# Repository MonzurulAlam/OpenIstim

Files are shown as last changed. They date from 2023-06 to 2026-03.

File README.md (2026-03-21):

# <P align="center"> OpenXstim - Open Source Transcutaneous Current Stimulator 
 
### DEVELOPED BY:
Dr Monzurul Alam <br/>
Profile: https://scholar.google.com.au/citations?user=a2yhqEQAAAAJ&hl=en&oi=ao <br/>
Contact: md.malam@connect.polyu.hk <br/>

### OBJECTIVES:
<P align="justify"> The objective of this project is to develop a miniature transcutaneous electrical stimulator for non-invasive muscle and nerve stimulation.

### DESCRIPTION:
<P align="justify"> Transcutaneous electrical spinal cord stimulation, a non-invasive spinal cord neuromodulation method holds tremendous promise and hope to restore functions in people with paralysis resultant of spinal cord injury (SCI), cerebral palsy (CP), stroke and other neurological conditions. Yet, there are not many options of such stimulation devices compared to conventional electrical stimulators such as neuromuscular electrical stimulator (NMES), transcutaneous electrical nerve stimulator (TENS) and functional electrical stimulator (FES), especially for most people with neurological conditions in the developing world.
<P align="justify">  OpenXstim is an open-source programmable electrical stimulator (constant current) is a non-invasive muscle, nerve or spinal cord stimulation device. OpenXstim can generate up to 128 mA current pulses with a compliance voltage up to 96 V per stimulation channel. The stimulator is capable of generating high-frequency (10 kHz) burst stimulation, required for transcutaneous spinal cord stimulation (tSCS).
<P align="justify"> The stimulator contains 5 primary sections: 1) a power management unit build with a few DC-DC converters to serve necessary power for the stimulator, 2) a Microcontroller unit for easy programming that provides necessary parameters for the stimulation, 3) a control and display unit to vary the stimulation parameters and display the values, 4) a Digital-to-Analog Converter (DAC) to generate voltage stimulation pulses, 5) a Voltage-to-Current converter unit to convert voltage pulses into appropriate current pulse.

Block-Diagram

### DISCLAIMER:
<P align="justify"> The design is offered as it is. Although it has been regorously tested with utmost care and to the best of my knowledge, I do not provide any warranty in any aspect.

### WARNING:
- The design is intended stricktly for research and education purposes.
- The stimulator is not approved for human or animal and cannot be used without receving prior approval from appropriate ethics committee such as Institutional Review Board.
- The stimulator can generate high voltage and under no circumstances it should be placed across the chest or close to the heart.
- The stimulator should never be powered from external adapter, USB or power source while being used or connected to the body.

### LICENSE:
##### Documentation licensed under the Creative Commons Attribution Share Alike (CC BY-SA) 4.0 International License

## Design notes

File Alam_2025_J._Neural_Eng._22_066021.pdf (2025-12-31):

## Journal of Neural Engineering

PAPER • OPEN ACCESS

## OpenXstim: an open-source programmable electrical stimulator for transcutaneous spinal cord stimulation therapy

To cite this article: Monzurul Alam et al 2025 J. Neural Eng. 22 066021

View the article online (https://doi.org/10.1088/1741-2552/ae20c2) for updates and enhancements.

## You may also like

Using a high-frequency carrier does not improve comfort of transcutaneous spinal cord stimulation
Ashley N Dalrymple, Charli Ann Hooper, Minna G Kuriakose et al.

Recording evoked potentials during deep brain stimulation: development and validation of instrumentation to suppress the stimulus artefact
A R Kent and W M Grill

Randomized cortical stimulation could ameliorate locomotive inability in Parkinsonian rats: a pilot study
Rong-Chao Peng, Xiu-Xiu Liu, Ya Ke et al.

This content was downloaded from IP address 175.32.55.112 on 27/11/2025 at 11:42

J. Neural Eng. 22 (2025) 066021 | https://doi.org/10.1088/1741-2552/ae20c2

# Journal of Neural Engineering

OPEN ACCESS

RECEIVED
22 September 2025

REVISED
2 November 2025

ACCEPTED FOR PUBLICATION
18 November 2025

PUBLISHED
27 November 2025

Original content from
this work may be used
under the terms of the
Creative Commons
Attribution 4.0 licence. (https://creativecommons.org/licenses/by/4.0/)

Any further distribution
of this work must
maintain attribution to
the author(s) and the title of the work, journal
citation and DOI.

PAPER

# OpenXstim: an open-source programmable electrical stimulator for transcutaneous spinal cord stimulation therapy

Monzurul Alam¹,2,∗, (https://orcid.org/0000-0003-0987-1999) Vaheh Nazari³
, Md Akhlasur Rahman⁴

, Vijayapriya Arumugam⁵
,
Naveena Narayanan⁵

, Farjana Taoheed⁴

, Md Shofiqul Islam¹, (https://orcid.org/0000-0001-8085-7976) Padmanabhan Thirunavukkarasu⁶ ,
Mohammad Sohrab Hossain⁴ (https://orcid.org/0000-0002-8452-1641) and Alistair McEwan²,7 (https://orcid.org/0000-0001-7597-6372)

1 Bangladesh Health Professions Institute, Savar, Bangladesh
2
School of Biomedical Engineering, University of Sydney, Sydney, New South Wales, Australia
3
School of Human Movement and Nutrition Sciences, University of Queensland, Brisbane, Queensland, Australia 4 Centre for the Rehabilitation of the Paralysed, Savar, Bangladesh
5 Braintree Speciality Clinic, Chennai, India
6 Madras Medical College, Government Institute of Rehabilitation Medicine, Chennai, India
7
Current address: Cerebral Palsy Alliance, The University of Sydney, NSW 2006, Australia
∗
Author to whom any correspondence should be addressed.

E-mail: md.malam@connect.polyu.hk

Keywords: non-invasive electrical stimulation, transcutaneous spinal cord stimulation (tSCS), neuromodulation, neurological injury, rehabilitation

Supplementary material for this article is available online (http://doi.org/10.1088/1741-2552/ae20c2)

Abstract
Objective. Transcutaneous spinal cord stimulation, a non-invasive spinal cord neuromodulation method holds tremendous promise and hope to restore functions in individuals with paralysis resulting from spinal cord injury (SCI), cerebral palsy, stroke and other neurological conditions. Yet, there are relatively few options for such stimulation devices compared to conventional stimulators commonly used for neuromuscular electrical stimulation, transcutaneous electrical nerve stimulation, and functional electrical stimulation, particularly for people with neurological conditions in the developing countries. Approach. In this report, we present OpenXstim, an open-source, twochannel programmable electrical stimulator developed to advance research in non-invasive muscle, nerve, or spinal cord stimulation treatments. Main results. OpenXstim can deliver current pulses up to 110 mA with a compliance voltage of 96 V per channel. In benchtop testing, we found that the stimulator successfully generates high frequency (9 kHz) burst stimulation, a mode commonly used for spinal cord neuromodulation. The stimulator was further tested in two individuals with SCI and showed preliminary indications of functional improvement. However, large controlled trials are needed to establish efficacy. Although special care was taken in the design of the stimulator to ensure user safety, users are strongly warned to handle the device with utmost caution, as it can generate high voltage and current that may cause adverse health effects if not used properly. Significance. This programmable, open-source stimulator offers tangible hope for improving the accessibility of non-invasive neuromodulation treatments for people with paralysis worldwide. The design and complete source-code of the stimulator are freely available online in a public repository: https://github.com/OpenMedTech-Lab/OpenXstim

### 1. Background

Transcutaneous spinal cord stimulation (tSCS) is an emerging non-invasive technique that has shown promising results in enhancing functional recovery across several neurological conditions, including spinal cord injury (SCI) (Tefertiller et al 2022,

Moritz et al 2024, Lucas et al 2025), cerebral palsy (CP) (Hastings et al 2022, Sachdeva et al 2024), stroke (Moshonkina et al 2022, Kreydin et al 2024), and traumatic brain injury (TBI) (Qian et al 2020, Calderone et al 2024). By delivering electrical stimulation through the skin to the spinal cord, tSCS aims to modulate spinal neural circuits and enhance

© 2025 The Author(s). Published by IOP Publishing Ltd

J. Neural Eng. 22 (2025) 066021 | M Alam et al

sensorimotor function. Evidence suggests that tSCS
can lead to significant improvements in movement, muscle strength, and overall functional outcomes, particularly when combined with conventional activity-based rehabilitation methods (Gopaul et al 2025, Suggitt et al 2025). For successful neuromodulation, a single rectangular pulse or burst of tSCS at motor-threshold elicits evoked potentials to the muscles through efferent synaptic pathways (Alam et al 2020, Gelenitis et al 2025). Previous studies have demonstrated that moderate-intensity tSCS applied over the T11-T12 vertebrae can depolarize posterior root and simultaneously elicit bilateral monosynaptic reflexes in the quadriceps, hamstrings, tibialis anterior, and triceps surae muscles (Sayenko et al 2015, Calvert et al 2019, Gordineer et al 2024). It was further demonstrated that monosynaptic posterior root reflexes in extensor and flexor muscles of thigh and leg can be elicited by stimulating L2-S1 spinal segments in upright standing position, and can be modulated during the execution of postural maneuvers (Hofstoetter et al 2018, Bryson et al 2023). Tonic tSCS utilizes charge-balanced, symmetric, biphasic rectangular pulses at sub-threshold strengths to modulate the spinal cord circuits. The frequency of this tonic stimulation generally ranges from 5 to 100 Hz. Recent design includes modulated tSCS with a 5–10 kHz carrier frequency, which can successfully activate spinal circuits in human (Gerasimenko et al 2015, Shamantseva et al 2024), although some studies have found no significant benefit of using high carrier frequencies over conventional waveforms (Manson et al 2020, Dalrymple et al 2023). Recent studies have found that, in case of a disruption of the connection between the brain and the spinal cord, resulting from an injury or disease, motor tasks can be enabled by tSCS to the cervical and/or lumbosacral segments of the spinal cord (Martin 2021, Rahman et al 2022, Alam et al 2023). Modification of spasticity by tonic tSCS was also demonstrated in individuals with SCI (Hofstoetter et al 2020, Alashram et al 2021, Minassian et al 2024). In a recent study, it has also been demonstrated that tSCS can induce rhythmic activities of legs in robotic orthosis driven body-weight support system in upright position in people with complete SCI (Minassian et al 2016, Krenn et al 2023). Furthermore, repetitive gait training along with tSCS promotes long term functional recovery (Esteset al 2021, Comino-Suárez et al 2025). Despite the growing success of tSCS in restoring functions in individuals with various neurological conditions, there are very few stimulators available that can deliver the specific stimulation parameters required—particularly high-frequency stimulation at 5–10 kHz. Furthermore, the ones that are available are expensive, bulky, and require careful laboratory setting and are not suitable for home or outdoor use. To address this a simple, low-cost, open source, programmable electrical stimulator was developed, and step-by-step prototyping of the stimulator was presented to allow others to make their own stimulator for tSCS therapy (Alam 2022). In the present report, an upgraded multichannel stimulator is presented which is capable of current pulse stimulation, crucial for more robust neuromodulation therapy. Several open-source electrical stimulators have been reported (Coelho-Magalh˜aes et al 2022, Trout et al 2023). But, to the best of our knowledge, this is the first open-source electrical stimulator capable of high frequency burst stimulation. Special care has been given to minimize the complexity of the design by using commonly available components so that one can build one’s own stimulator from anywhere in the world. In this report, we have also included two case studies in which participants demonstrated improvements in sensorimotor function following stimulation treatment using the OpenXstim stimulator.

### 2. Methods

### 2.1. Stimulator design

For easy prototyping, the electrical stimulator was designed using commonly available commercial offthe-shelf components. Functional block diagram of the stimulator is shown in figure 1. The stimulator contains 5 primary sections: (1) a power management unit build with a few DC–DC converters to serve necessary power for the stimulator, (2) a Microcontroller unit for easy programming that provides necessary parameters for the stimulation,
(3) a control and display unit to vary the stimulation parameters and display the values, (4) a digital-toanalog converter (DAC) to generate voltage stimulation pulses, (5) a voltage-to-current converter unit to convert voltage pulses into appropriate current pulse. Operations of each of these are described in detail in the following sections.

### 2.2. Power management by DC–DC converters

The stimulator requires different voltages and power ratings for different sections. For instance, while the Microcontroller and display unit require only positive rail, the DAC and V/I circuit require both positive and negative rails to operate. Furthermore, due to the high skin impedance (∼500 Ω at 1 kHz), transcutaneous stimulation requires high compliance voltage to be able to deliver necessary current through the skin. But, for safety and ease of use, these stimulators are commonly powered by a single NiCd/NiMH battery. The presented stimulator is powered by a single 9 V battery with relatively high ampere-hour ratings (>650 mAh) to be able to deliver necessary power. Figure 2 shows the power management circuit of the stimulator. The battery voltage is inverted to negative rail using a charge pump DC–DC converter

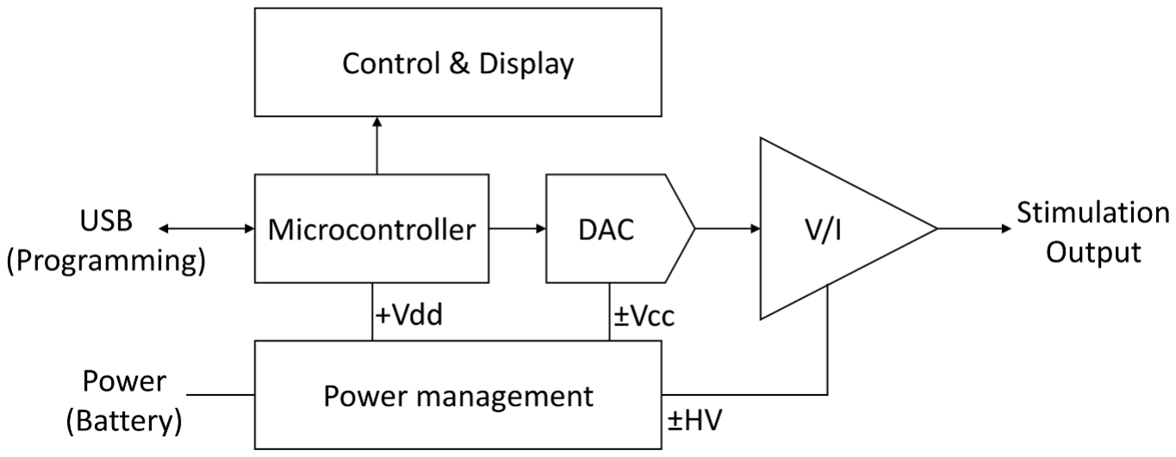
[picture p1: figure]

Figure 1. Block diagram of a transcutaneous electrical stimulator (OpenXstim) for non-invasive electrical stimulation. The stimulator has 5 major sections: a power management unit to serve necessary power for the stimulator, a Microcontroller unit for easy programming stimulation parameters, and a control & display unit to set and display the stimulation parameters, a digital-toanalog converter (DAC) to generate stimulation pulses, a voltage-to-current (V/I) converter unit to convert voltage pulses into appropriate current pulses.

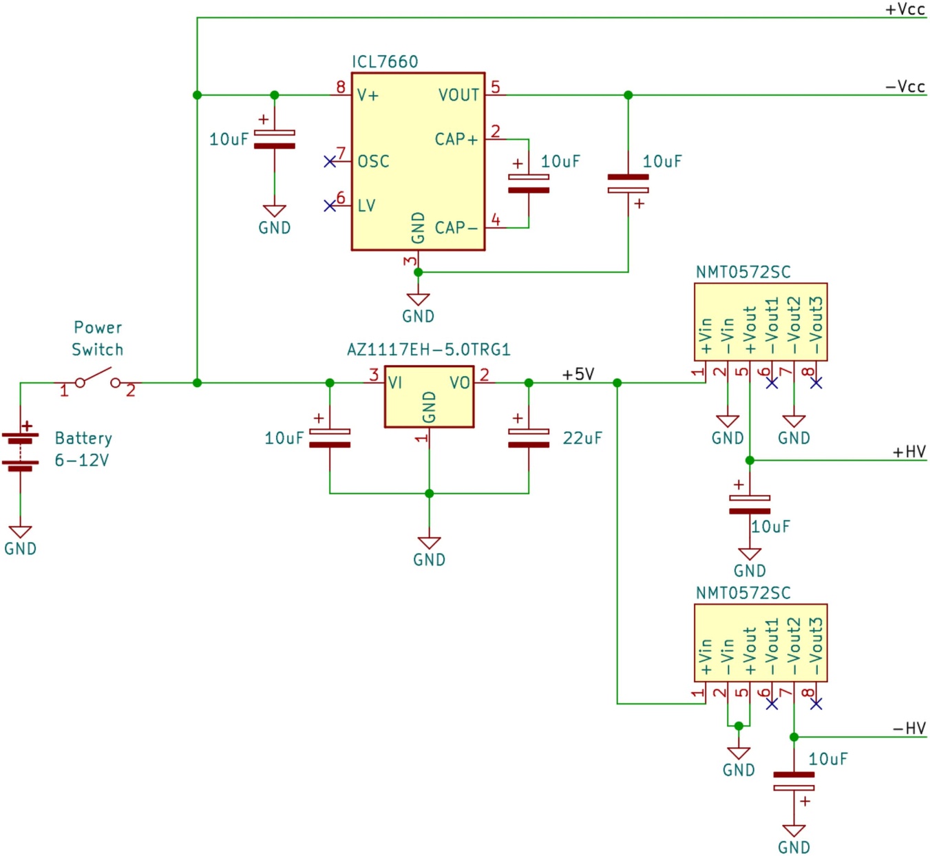
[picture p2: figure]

Figure 2. Schematic diagram of the power management circuit of OpenXstim stimulator. While the circuit allows any voltage between 6 to 12 volts to have stable operation, we recommend using a 9 V 650 mAh battery to power the stimulator.

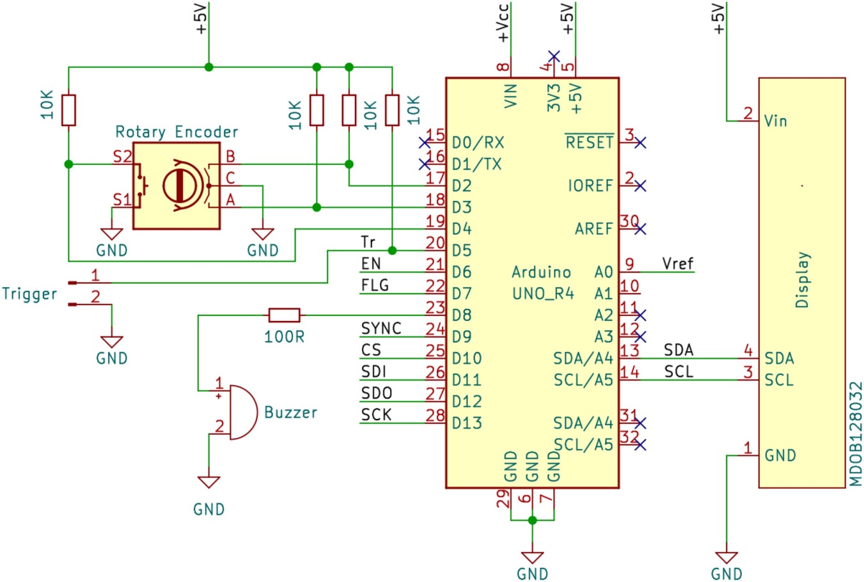
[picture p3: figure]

Figure 3. A rotary encoder and a display unit are wired to Arduino Uno Microcontroller board for quick change and display the stimulation parameters. A digital buzzer is also connected to the Microcontroller to allow audio notifications for different events as per programmed.

(ICL7660S) for the DAC circuit to be able to generate biphasic stimulation pulses. In parallel, to generate high voltage rails, two isolated DC–DC boost converters (NMT0572SC) are used. The boost converters are connected in such a manner to produce both high positive (+HV) and high negative (−HV) voltages. We used the -vout2 of NMT0572SC to get 48 volts rail for V/I converter circuit. A high-voltage 10 µF capacitor was used on each rail to store charge for high-current operation during the active cycle of the stimulation. Since the DC–DC boost converters can only operate with 5-volt input, we used another DC– DC voltage regulator (AZ117EH-5.0TRG1) to power both NMT0572SC. Necessary capacitors with appropriate voltage and charge ratings were used to regulate the voltage for each DC–DC converter chip. For details, please refer to appropriate datasheet provided by the chip manufacturer.

### 2.3. Set and display stimulation parameters

(Microcontroller, Control and display unit)
The core of the stimulator is a very popular open-source Microcontroller board: Arduino Uno. While necessary firmware can be uploaded to the Microcontroller from a computer using a standard USB cable to run the stimulation program, a digital rotary encoder (PEC12R-4025F-S0024) was used to allow quick parameter changes. A rotary encoder typically uses a rotating disk with patterns and a magnetic sensor to produce pulses as the disk turns. Taking advantage of two interrupt pins of Arduino Uno (figure 3 shows the wiring diagram), the output signals of PEC12R-4025F-S0024 rotary encoder sends the microcontroller to specific interrupt service routine (ISR) to increase or decrease output current. This method ensures precise and efficient handling of the encoder’s output by responding immediate pulse changes. The rotary encoder also includes a built-in press-switch function, which allows switching between current intensity and frequency adjustment modes. Pressing the knob activates a subroutine in the firmware (supplementary 1) that enables frequency control using the same rotary count mechanism. The stimulation parameters and other information are displayed to an OLED display (MDOB128032) connect via the I2C bus of the Microcontroller. We used SSD1306 display driver, developed by Adafruit for the OLED display. Figure 3 shows the complete wiring diagram of the PEC12R-4025F-S0024 rotary encoder and MDOB128032 display to the Microcontroller.

### 2.4. Biphasic pulse generation by DAC

To generate bipolar output voltage, a dual channel 12-bit Digital to Analogue Converter (AD5722) was used. The DAC is controlled through a standard 4-wire serial peripheral interface bus. Figure 4 shows the wiring diagram of AD5722 for Arduino Uno Microcontroller. A voltage divider made by two 1k

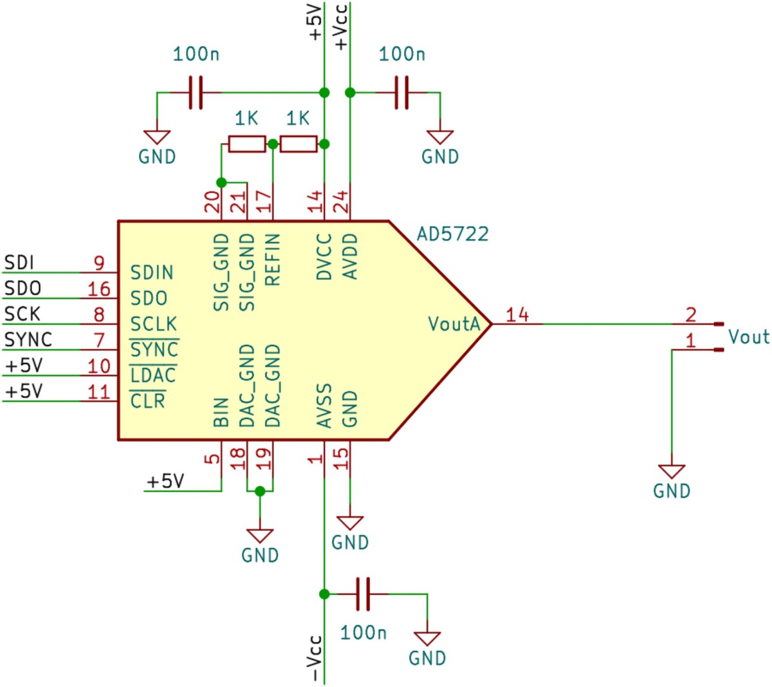
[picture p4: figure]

Figure 4. Schematic diagram of AD8722, a dual channel 12 bit digital-to-analog converter (DAC). For simplicity, only one channel is shown (VoutA).

resistors was used to supply the reference voltage. As mentioned in the power management section, the DAC is supplied with both positive and negative analogue power rails (±5 V) to allow it to generate bipolar voltage stimulation. For bipolar output range, the output voltage expression for AD5722 is shown below:

VOUT = VREF × Gain D
2

N

−

Gain × VREF
2

(1)

where:

D is the decimal equivalent of the value loaded to the DAC
N is the bit resolution (12)
VREF is the reference voltage applied to the REFIN pin (2.5 volt)
Gain is the internal gain (set to 4 for ±5 V output span)

### 2.5. Generating current pulses by

voltage-to-current (V/I) converter
The bipolar voltage output from each DAC channel is converted to constant current using an improved Howland current pump circuit (figure 5). A high-voltage (100 V), high-current (50 mA) operational amplifier (OPA454) was used to deliver the required high rating current pulses for the stimulator. Current pulses were generated by alternating the input voltage (Vin) of the improved Howland current pump circuit. This is done by programming the DAC to output alternating voltages at a stimulation frequency. We also used highly matched 25 kΩ (±0.1%) resistors array (ORNTA2502AT1) to convert the input voltage into a precise output current. In this V/I converter circuit, matched resistors are crucial for maintaining accuracy and stability. The op-amp in the circuit controls the current through the load based on the ratio of the resistors. A 50 Ω current control resistor (Rx) was used to set-up voltage-to-current ratio as shown in the following equation:

IOUT ≈

Vin
Rx

(2)

where:

(R4 + Rx)/R2 = R3/R1;

Ideally, when both positive and negative feedback of the operational amplifier are balanced, an infinite output impedance is achieved. As a result, the output current is simply the ratio of the input voltage to the input impedance which is primarily determined by the current control resistor (Santos et al 2013).

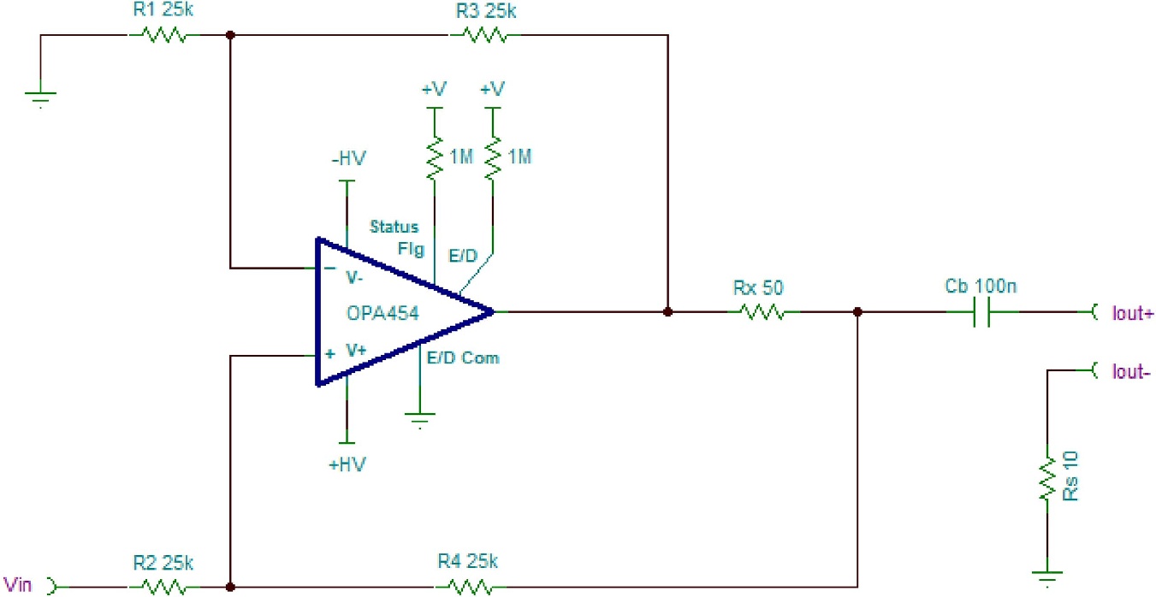
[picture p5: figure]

Figure 5. Improved Howland current pump using high-voltage high-current operational amplifier (OPA454) working as a precise voltage-to-current (V/I) converter circuit. A 25 kΩ quad matched resistor array (ORNTA2502AT1) is necessary to provide stable output current for the stimulator.

Two 1 MΩ pull-up resistors are also required for correct operation of the OPA454 operational amplifier. A 100 nF blocking capacitor is warranted for the protection of DC current to pass through the stimulation electrode in case the stimulator malfunctions. This is an important safety measure one should follow for electrical stimulation of biological tissues (Merrill et al 2005, van Dongen and Serdijn 2016). The stimulation current was also passed through a 10 Ω current sense resistor to allow continuous monitoring of the stimulation pulses.

### 2.6. Prototyping the stimulator

Step 1: Develop and assemble stimulator shield board The complete schematics of the stimulator shield board was developed using an open-source electronic design automation (EDA) software (KiCAD 6.0). Gerber files were generated for prototyping the printed circuit board (PCB) of the stimulator shield board. A two-layer PCB was prototyped through a PCB manufacturer service (JLCPCB, Hong Kong SAR). All the components were sourced and assembled on the PCB through hand soldering. Figure 6(a) shows the 3D model of the assembled stimulator shield board. Standard male header pins were soldered on the bottom of the shield board to allow it to mount on the Microcontroller development board.
Step 2: Stack the stimulator shield on an Arduino Uno board and housing the assembled stimulator
The stimulator shield board was developed with the same footprint of an Arduino Uno development board so that it can easily be stacked on it (figure 6(b)). Arduino Uno is probably the most popular and widely available open-source Microcontroller board, allowing our stimulator to be taken up in most places around the world. Arduino Uno already has onboard female header pins allowing a shield board to be easily mounted on it.
The next step of prototyping is to build a case to house the stimulator to protect the electronics and the users from accidentally touching the components during its operation. We used a computer aided design software (SolidWorks, USA) to design the stimulator’s case, knob, and switch. First, we extracted a 3D model of the stimulator board using EDA software (KiCAD 6.0, USA). The model was then imported into the assembly document, where we began designing the bottom part of the case by creating a new part. The base outline was sketched based on the board’s dimensions; and then extruded to generate a 2 mm thick base. We then added the walls of the case by sketching an outline on the base followed by extrusion to desired height. Functional openings for ventilation and component connections were created. This process was repeated for all components, with each model saved and printed using PLA material on a 3D printer (Adventurer 3, Flashforge, China). Figure 6(c) shows an exploded view of the stimulator.
Step 3: Program the Stimulator
To program the Microcontroller, the Arduino Uno board was connected to a PC via a USB cable. After successfully selecting Arduino Uno board from the menu of Arduino IDE, the firmware was downloaded into the Microcontroller. The program flowchart

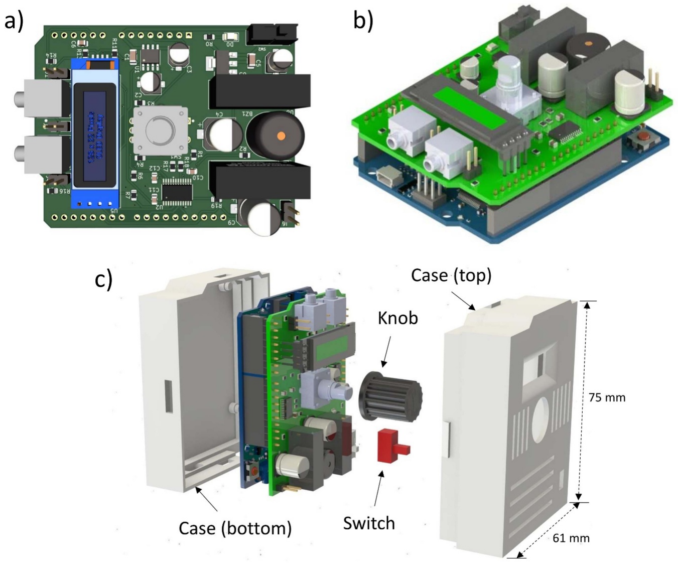
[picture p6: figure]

Figure 6. (a) 3D electronic design automation (EDA) model of assembled stimulator shield board. (b) Stimulator shield board stacked on an Arduino Uno Microcontroller development board through standard header pins. (c) Stimulator case, knob and switch printed using a 3D printer to house the stimulator board.

is shown in figure 7. After the start, stimulation parameters including stimulation frequency, pulse width, burst duration etc. are defined. Next, all the hardware connected to the Microcontroller are initialized by calling appropriate libraries. Then, in a loop N number of biphasic stimulation pulses are generated by writing the defined value to the DAC register. After this loop of stimulation (active burst burst), a delay (inter-burst delay calculated based on the defined stimulation frequency) was added to complete the stimulation cycle. The entire process runs again and again to repeat the stimulation indefinitely until it is powered off.
An ISR was also defined to allow the user quickly to change the stimulation intensity and frequency without re-programming the Microcontroller. Once the rotary encode is rotated, it initiates hardware interrupt of the Microcontroller which triggers the program to break the continuous main loop and jump into the ISR. In the ISR, the program increments or decrements the variable base on the data it reads from the rotary encoder. After that the program returns to the main loop, but now with the updated value of the variable which essentially reflects on the stimulation (an increased or decreased stimulation intensity). The entire source code of the firmware is shared in the stimulator’s GitHub repository as well as attached in supplementary 1.

### 2.7. Benchtop testing the stimulator

The stimulator tested on a benchtop setup. Figure 8 shows the experimental setup. The stimulator was powered by a 9 V battery using barrel adapter. The outputs were connected to two loads, one is 100 Ω resistor and the other is a Randles equivalent circuit of human skin (∼500 Ω impedance at 1 kHz) to test the functionality of the stimulator and emulate the expected operating conditions. A dual channel oscilloscope was used to monitor the voltage across the loads as well as to record the stimulator’s output signal. Stimulation current was varied from 0–140 mA at 20 Hz stimulation (packed with 10 burst pulses at 9 kHz). Data from the oscilloscope were recorded and analyzed to assess the performance of the stimulator in terms of its current, waveform shape, and frequency.

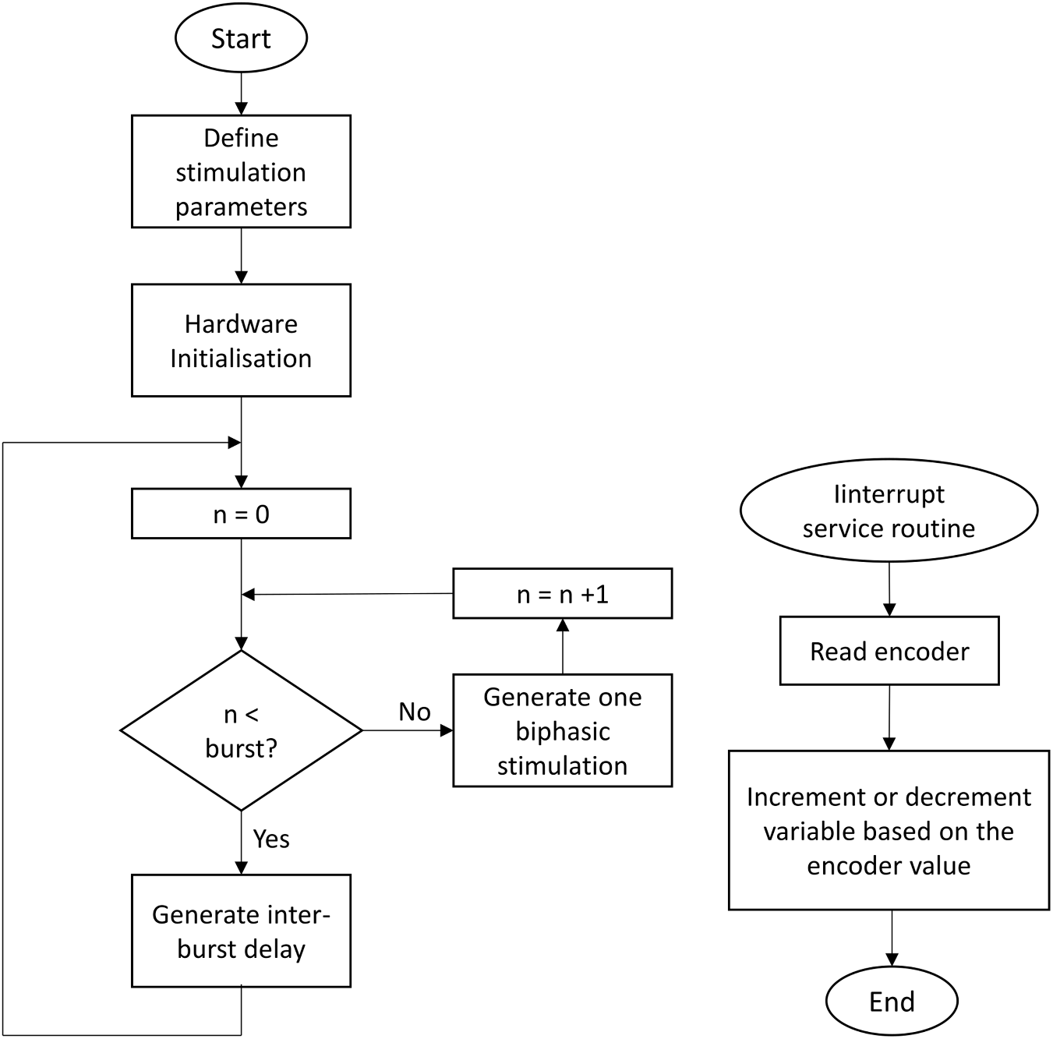
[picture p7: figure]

Figure 7. Flowchart of the high frequency stimulation program.

### 2.8. Clinical case studies

To test the stimulator, we conducted a series of clinical case studies involving individuals with chronic SCI (Trial registration No. ACTRN12625001081404). Eligible participants were required to be at least oneyear post-injury, medically stable, and have previously completed a course of conventional physiotherapy without significant neurological improvement. Individuals with uncontrolled comorbidities, open wounds at stimulation sites, implanted electrical devices, or contraindications to electrical stimulation were excluded. The aim was to evaluate the device’s ability to safely deliver tSCS in combination with conventional physiotherapy, assess participant comfort and tolerance, and observe any preliminary functional changes in a feasibility context. Two self-adhesive stimulation electrodes with a diameter of 3.2 cm (ValuTrode, Axelgaard Manufacturing Co. Ltd) were placed over the interspinous space between T11-T12 and L1-L2, and two internally connected

6.0 × 9.0 cm self-adhesive rectangular return electrodes (Guangzhou Jetta Electronic Medical Device Manufacturing Co. Ltd, China) placed above the iliac crests (Alam et al 2020). Before each stimulation session, the skin was checked to ensure it was free from irritation or wounds. Electrodes were placed with full adhesion and monitored throughout to maintain conductivity and prevent discomfort. These precautions helped minimize the risk of skin irritation or burns during stimulation. Figure 9 shows the electrodes placement and stimulation pattern used for the studies. To ensure safety, standard clinical monitoring was performed throughout each stimulation session to detect any signs of discomfort. During the initial sessions, stimulation was applied at lower intensities and for shorter durations, with gradual increases based on participant tolerance. The electrode sites were inspected regularly before and after each session for any signs of skin irritation or redness.

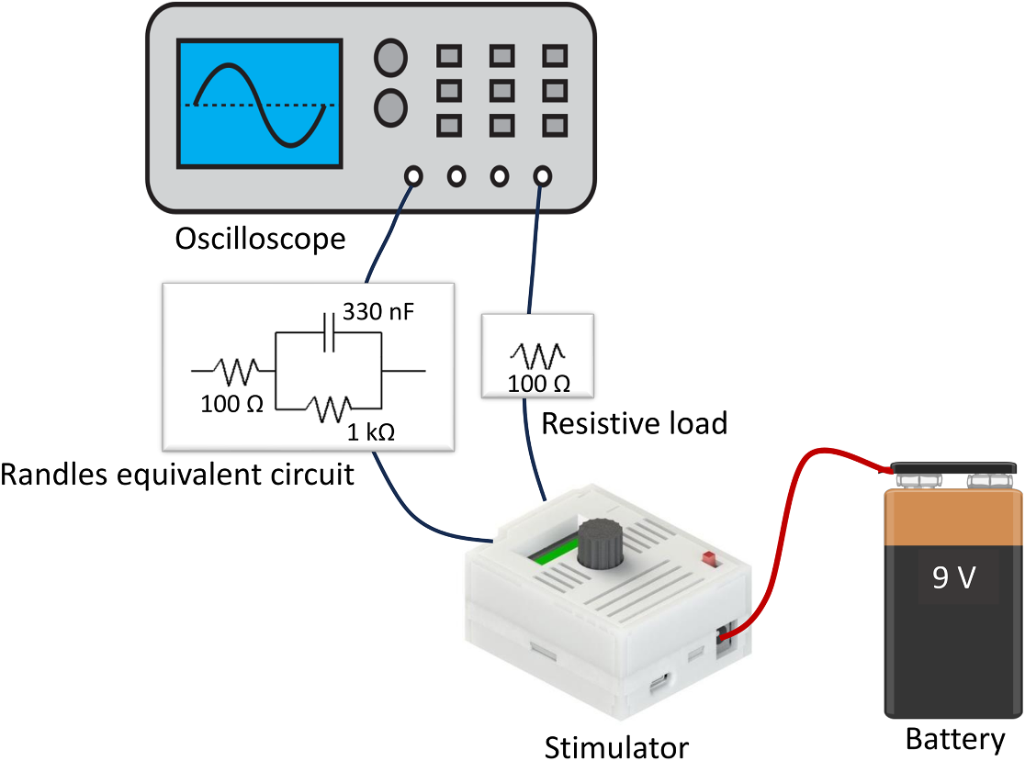
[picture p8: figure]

Figure 8. Benchtop setup for testing the functionality of the OpenXstim stimulator. The stimulator is powered by a 9 V battery. The output channels of the stimulator were connected to an oscilloscope through a resistive load (100 Ω) and Randles equivalent circuit (a 330 nF capacitor and a 1 kΩ resistor in parallel, connected in series with a 100 Ω resistor).

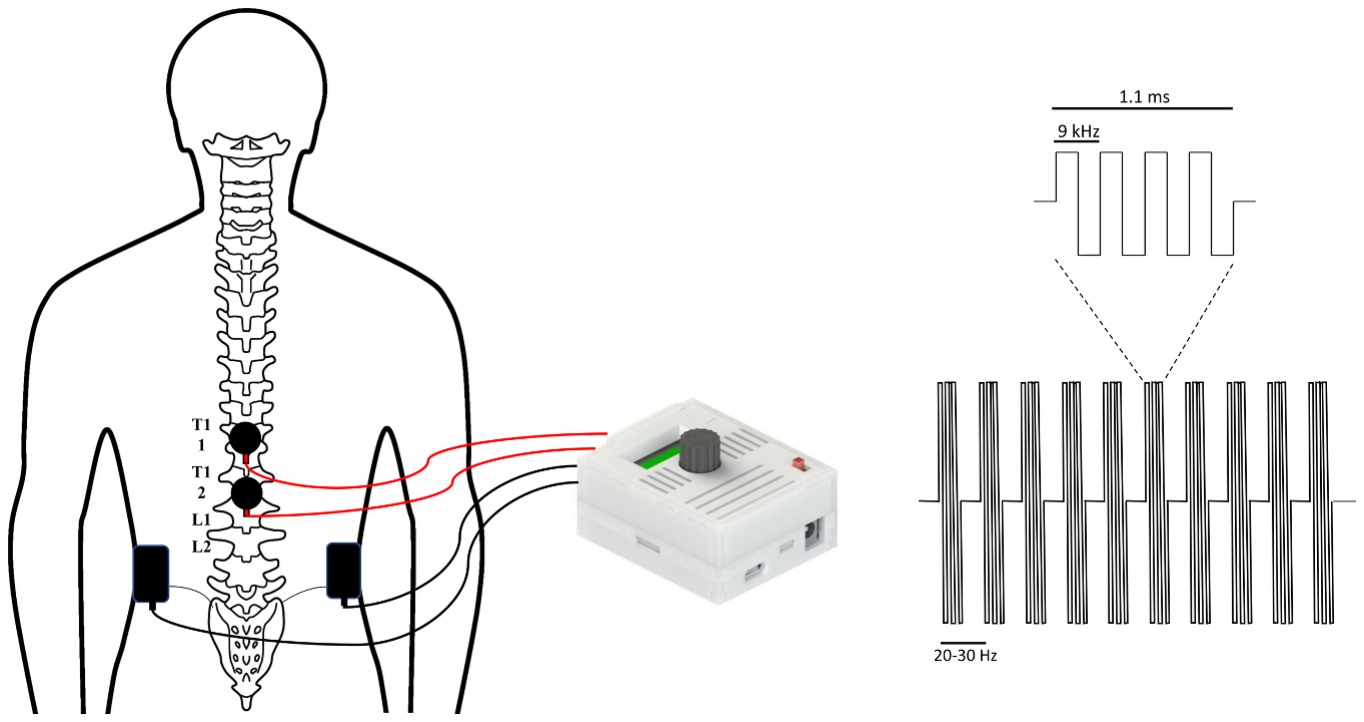
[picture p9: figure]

Figure 9. Electrodes placement of the OpenXstim stimulator (left) and high-frequency burst stimulation pattern (right) used for tSCS therapy.

Case 1:
The study participant was a 16 years old female who sustained a sensorimotor complete (ASIA-A) paraplegia following surgery for an arteriovenous malformation diagnosed at the thoracic 4 (T4) spinal cord. Post-surgery, she received regular physiotherapy upon being released from the hospital after her condition was stabilized. However, her sensorimotor condition did not change, and her paraplegia was considered permanent. Figure 10 shows the study procedure. The study was conducted in accordance with the Declaration of Helsinki and approved (Ref. CRP-BHPI/IRB/04/2025/1054) by the human research ethics subcommittee of the Centre for the Rehabilitation of the Paralyzed, Savar, Bangladesh. At the beginning of the study, a certified physiotherapist assessed the study participant for her sensorimotor scores according to the International

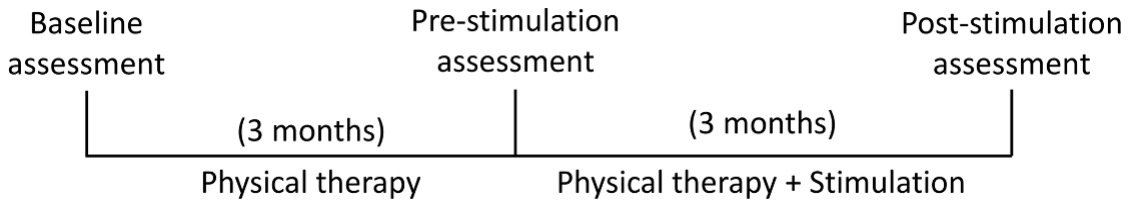
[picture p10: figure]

Figure 10. Study procedure. After baseline assessment of International Standards for Neurological Classification for SCI (ISNCSCI) for residual sensory and motor function, the study participant received conventional physical therapy for a period of 3 months followed by another ISNCSCI assessment. The study participant was then treated with transcutaneous spinal cord stimulation (tSCS) along with the same physical therapy for another 3 months. After the completion of this combinational treatment a final assessment was conducted.

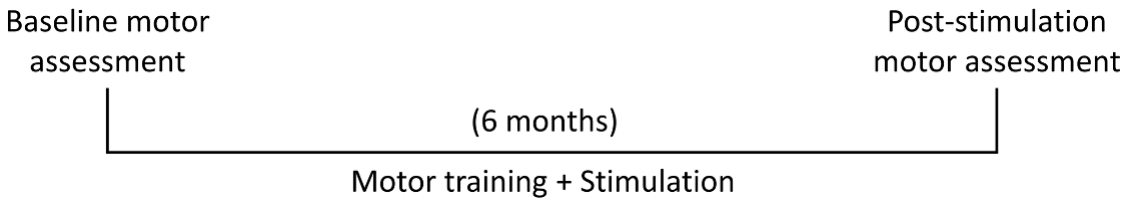
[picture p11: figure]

Figure 11. Study procedure. After baseline motor assessment (MAS), the study participant received a combinational treatment of motor training along with transcutaneous spinal cord stimulation (tSCS) for a period of 6 months. After the completion of this treatment a final motor assessment (MAS) was carried out.

Standards for Neurological Classification for SCI (ISNCSCI). The same physiotherapist also assessed her two more times: at 3 month and 6 month timepoints. During the first phase of treatment, the study participant received a conventional physiotherapy for about 35 min, 3 times a week for 3 months: first 15 min session was sitting balance practice (both static and dynamic condition), then 5 min rest and second 15 min session was standing and sitto-stand practice with the assistance of the physiotherapist. After a thorough sensorimotor assessment (ISNCSCI), in the second phase of the study, the participant received the same physiotherapy but with stimulation tSCS at T11 and L1 spinal levels at 20 Hz, packed with 9 kHz biphasic pulses. The stimulation current was set to a current level that was comfortable to the study participant (40–60 mA) during the physiotherapy session. At the end of the study, the study participant was again assessed (ISNCSCI) for her sensorimotor changes by the same assessor.

Case 2:
A 43 years old female with no significant comorbidities sustained a traumatic SCI following a fall that resulted in a fracture of the T11 spinous process. A posterior spinal fusion from T10 to L1 was performed within 24 h. Post-surgery, she was diagnosed with both motor and sensory complete SCI (ASIA-A) paraplegia, which improved to T11 by discharge. Since her recovery, she had undergone functional electrical stimulation (FES) cycling 1-3 times per week and body-weight supported treadmill walking twice a day. At 2 years post-injury, the ISNCSCI assessment showed limited muscle function: the bilateral hip flexors were graded at 1/5, with very faint movement on the left side. The right knee extensors also showed minimal function, graded at 1/5. All other muscle groups tested were graded at 0/5, indicating no muscle activity in those areas. Figure 11 shows the study procedure. The study was conducted in accordance with the Declaration of Helsinki and was approved (Ref. IEC-MMC/Approval/04032024) by the Institutional Ethics Committee, Madras Medical College, Chennai, India.
At the beginning of the study, a certified physiotherapist assessed the study participant for her sitting function according to the Motor Assessment Scale (MAS). Same physiotherapist also assessed her after 6 month of stimulation assisted motor training. The stimulation intensity and frequency were adjusted according to the task to achieve the desired response. The study participant underwent training 3–5 d a week, focusing on tasks such as sit-to-stand (20 Hz, 30 mA biphasic stimulation), trunk dynamic balance in sitting (20 Hz, 50–70 mA biphasic stimulation), and body-weight supported gait training (30 Hz, 30 mA biphasic stimulation), with each session lasting 20–30 min. The study was approved (Ref. IEC-MMC/Approval/04032024) by the Institutional Ethics Committee, Madras Medical College, Chennai, India.

### 3. Results

### 3.1. OpenXstim: A light-weight versatile stimulator

OpenXstim is an open-source programmable current pulse stimulator capable of transcutaneous stimulation. Figure 12 shows the prototyped stimulator. The stimulator was lightweight (<100 gm), portable

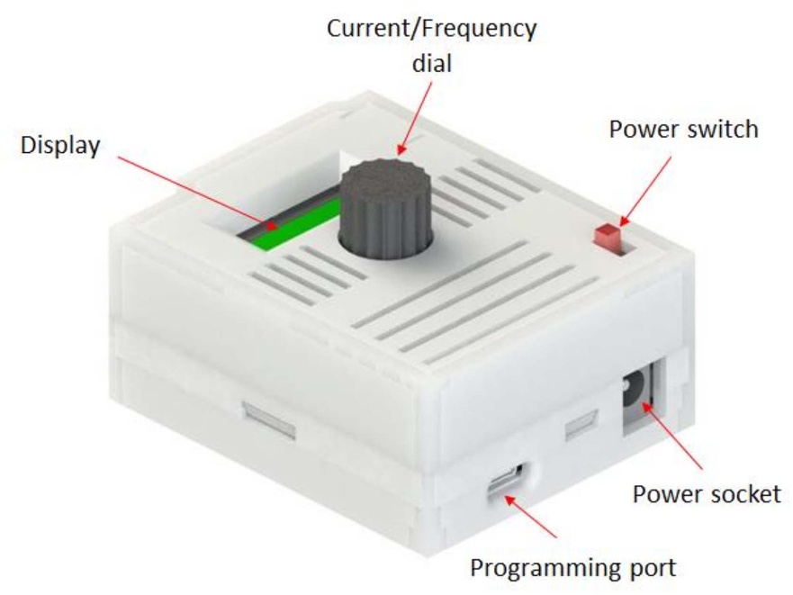
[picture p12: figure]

Figure 12. OpenXstim, open-source transcutaneous electrical stimulator. The stimulator can be powered by a 6–12 V battery with standard barrel jack. Power switch enables the output to deliver stimulation current. The current intensity and frequency are varied using the dial (black) in the center—mode can be selected by pressing the dial knob. The set value is dynamically displayed on the screen of the stimulator.

Table 1. Specifications of the OpenXstim transcutaneous electrical stimulator.

Channel count | 2 channels
Mode of operation | Current pulse
Stimulation waveform Monophasic/Biphasic
| (programmable)
Stimulation intensity | 0–110 mA
Compliance voltage | Maximum 96 V (peak-to-peak)
Pulse duration | Minimum 50 µs (programmable)
Stimulation frequency Maximum 9 kHz (programmable)
Power supply | 6–12 V DC

(battery powered), and easy to use, with participants and clinicians finding it simple to transport and operate. The rotary knob control made to adjust the current and the frequency was straightforward, and the therapists reported no difficulties in using the device. The stimulator was compact enough to be carried and placed in the required treatment locations, and there were no issues with the electrode or cable during the study. The device performed reliably over the six-month usage period, demonstrating strong feasibility and usability. However, an improvement could be made with the battery design—having a built-in, rechargeable battery would eliminate the need for frequent replacements and enhance the overall user experience. Detailed specifications of the stimulator are listed in table 1.

### 3.2. OpenXstim can generate high frequency burst

stimulation
In the present study, both channels of the stimulator were programmed to deliver high frequency burst pulses in-phase for transcutaneous electrical stimulation. The stimulator was tested on a benchtop setup; each channel of the stimulator connected to a load (see Methods section) for its functionality. Figure 13 illustrates the induced voltage across the load for 100 mA stimulation current. Ch 1 is the voltage across the Randles equivalent circuit whereas Ch 2 is the voltage across the resistive load. Both signals show successful biphasic burst stimulation at around 9 kHz.
The biphasic stimulation burst generated by the OpenXstim stimulator contains very short (<1 ns) inter-pulse interval due to the very fast operation of its DAC (see figure 13), a significant improvement from a commercial research stimulator (DS8R, Digitimer, United Kingdom) commonly used for transcutaneous stimulation where minimum inter-pulse interval is 1 µs. Furthermore, unlike many commercial electrical stimulators that uses multiplexed timesharing stimulation of multichannel stimulation (Valtin et al 2016), both stimulation channels of OpenXstim can stimulate simultaneous, providing greater flexibility of stimulation therapy.
The stimulator was also tested for its functionality of delivering required stimulation current at different intensities. Figure 14 shows the set vs measured stimulation currents across two loads. The results show excellent linear fits (R

2 = 0.9987 and 0.9997) of measured current values. However, the current does not appear to reach the set value, indicating a calibration offset. For the stimulation treatment, the current intensity was much lower than the maximum value.

Case 1: Restoration of somatosensory function using OpenXstim stimulator
Our study participant suffered a sensorimotor complete (ASIA-A) paralysis and received conventional
physiotherapy | followed | by | a | combinational

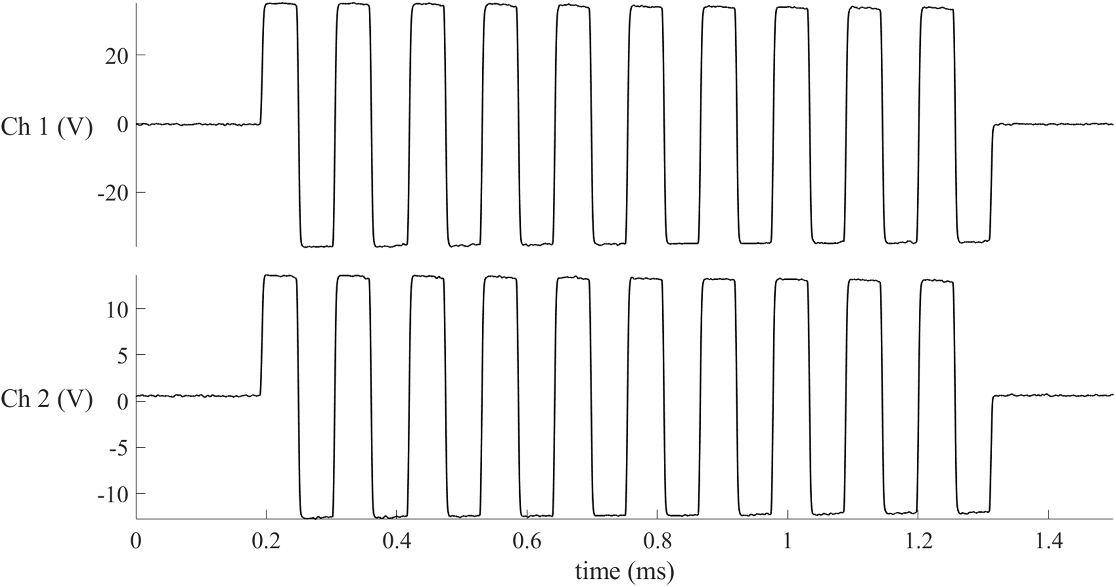
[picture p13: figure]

Figure 13. Induced voltage of 10 biphasic stimulation pulses at around 9 kHz burst stimulation across a Randles equivalent circuit (Ch 1) and a resistive load (Ch 2).

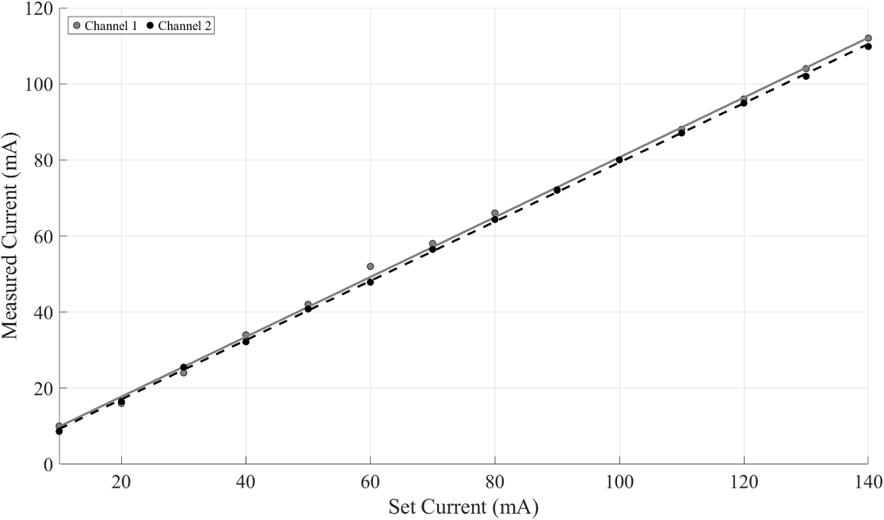
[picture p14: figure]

Figure 14. Set vs measured stimulation currents across loads. Blue line fits the data points measured for Channel 1 and black line fits the data points measured for Channel 2.

physiotherapy and tSCS. After 3 months of conventional physiotherapy (conservative management) without electrical stimulation, the ISNCSCI score remained the same as the baseline (motor and sensory complete ASIA-A). But after 3 months of physiotherapy with tSCS ASIA scale changed to ASIA-B (motor complete but sensory incomplete). Furthermore, the study participant got some sensory improvements as shown in figure 15. By the end of the study her sensory level for neurological injury changed from T4 to T5.
The tSCS therapy delivered by the OpenXstim was found to be well-tolerated, with preliminary indications of sensory improvement below the level of injury. The stimulation current was generally well-tolerated; however, due to the participant’s young age and unfamiliarity with the intervention, initial nervousness was reported in response to the novel sensations induced by tSCS. Over time, with continuous support and reassurance from the caregiver and clinician, the participant gained confidence and became increasingly comfortable as the study progressed.

Case 2: Improvement of motor functions after tSCS therapy
After 6 months of motor training with tSCS therapy delivered by the OpenXstim stimulator, the study participant showed improvements in sitting balance with forward weight shifting, and the study participant is now able to reach forward with better

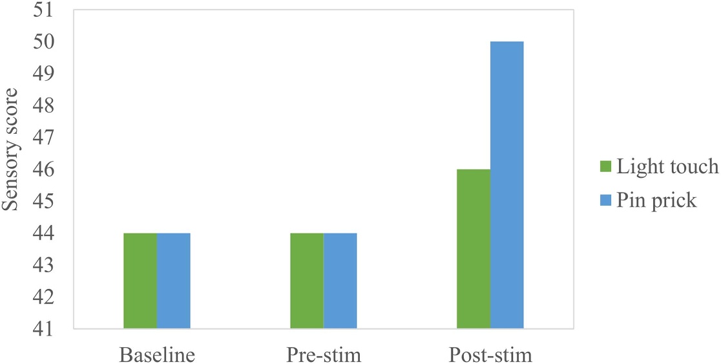
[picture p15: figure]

Figure 15. Total light touch and pin prick sensory scores according to the ISNCSCI at baseline, after 3 months conventional training (pre-stimulation) and 3 months conventional plus stimulation training (post-stimulation).

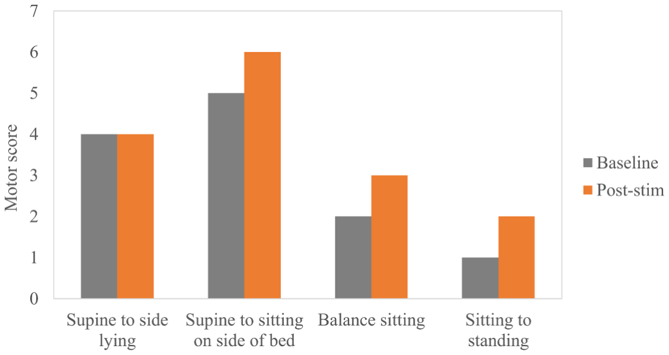
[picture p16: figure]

Figure 16. Baseline vs post-stimulation scores according to the Motor Assessment Scale (MAS) for different posture transitions.

core stability. Figure 16 shows changed in balance sitting and performance in postural transitions (supine to side lying, supine to sitting on the side of the bed and sitting to standing) before and after stimulation assisted motor training according to the MAS. Except supine to side lying, all other functions have improved after the stimulation training.
The tSCS was found to be feasible and safe, with early signs of improved core stability. The stimulation current was generally comfortable; however, when the battery charge depleted, it was not possible to lower the intensity before switching off the stimulator. This direct shutdown caused discomfort for the study participant, highlighting the importance of using high-rate battery that allows slowly reducing intensity prior to turning off the device.

### 4. Discussion

### 4.1. Clinical significance and the need for

accessible neuromodulation devices
Each year, an estimated 250 000–500 000 new cases of SCI are reported globally (Nuechterlein et al 2023), often resulting in life-altering and debilitating conditions. Recent studies have highlighted the potentials of tSCS as an effective neuromodulation therapy not only for SCI rehabilitation (Hofstoetter and Minassian 2022, Rahman et al 2022) but also for a range of neurological conditions, including CP (Gad et al 2021, Hastings et al 2022), TBI (Qian et al 2020, Calderone et al 2024) and Stroke (Moon et al 2024, Zhang et al 2024). Despite its growing therapeutic promise, access to tSCS remains limited due to the high cost, bulkiness, and proprietary nature of most available stimulators. In this report, we present

Table 2. List of electrical stimulators used for non-invasive spinal cord stimulation (tSCS) therapy.

Name | Company | Approval | Channel | Power | Price
Biostim-5 (Grishin et al 2019) | Cosyma Inc. | N/A | 5 | Battery | N/A
NeoStim-5 (Parhizi et al 2021) | | N/A | 5 | Battery | N/A
ARCEX (Samejima et al 2022) | ONWARD
| Medical Inc | FDA | 4 | Battery | N/A
Stimulette r2x (Hofstoetter et al 2021) | Schuhfried
| Medizintechnik
| GmbH | N/A | 2 | Line | N/A
SCONE™ (Kreydin et al 2022) | SpineX Inc. | FDA Breakthrough
| | Device | 2 | Battery | N/A
SCiP (Gad et al 2021) | | | 2 | Battery | N/A
DS8R (Alam et al 2020) | Digitimer Ltd | N/A | 1 | Line | £8,335
OpenXstim | Present report | N/A | 2 | Battery | <$200

OpenXstim, a low-cost, open-source transcutaneous
electrical stimulator designed to improve the accessibility and affordability of spinal cord stimulation— particularly in low- and middle-income countries (LMICs).

### 4.2. Bridging the gap: OpenXstim for global

research equity
The overarching aim of this work is to enhance research capacity, particularly within low-resource settings, by offering an affordable and openly accessible transcutaneous electrical stimulation platform in line with the 2030 UN Sustainable Development Goals. Financial constraints and limited access to proprietary technologies are two major barriers that continue to hinder research and development in these regions, despite the presence of substantial technical expertise and scientific talent (Leal Filho et al 2022). By addressing these barriers, this work seeks to catalyze innovation and enable researchers—especially in LMICs—to design and conduct ethically approved studies using a device tailored to their specific needs. Since the presented stimulator is fully programmable and supports and supports a wide bandwidth of stimulation parameters, it can be easily configured to deliver standard protocols including neuromuscular electrical stimulation, transcutaneous electrical nerve stimulation, and FES, as well as experimental paradigms such as high-frequency tSCS. Table 2 shows the list of transcutaneous electrical stimulators used for non-invasive spinal cord stimulation therapy in people with neurological conditions.

### 4.3. Open-source commitment and design

affordability
The presented stimulator (OpenXstim) provides an easy-accessible tool for non-invasive spinal cord stimulation to arguably for most communities around the world. The design schematics and source code for the stimulator are freely available online, allowing others to replicate or modify the device. All the design files, code and technical details can be freely downloaded from the OpenMedTech-Lab’s

GitHub repository (https://openmedtech-lab.github.io/). (https://openmedtech-lab.github.io/) This open-source approach is a significant step toward making spinal cord stimulation therapy more affordable and accessible, particularly in resourcelimited settings.
Components and modules used to build the OpenXstim stimulator are all listed in table 3. The total component cost of building the stimulator was only US$149.99; however, it can vary based on the market and supplies of the items. Additional costs should be considered for PCB prototyping and 3D printing of stimulator housing, which are significantly lower these days due to worldwide prototyping services. Reference prices and sources of all the components are also listed in table 3. Special care is given to choosing the most commonly available items so that anyone can build the stimulator anywhere in the world. One should, however, check with their local market and supplier for the availability of the components and modules. In case of unavailability, a similar module can be used, but care must be given to connect appropriate circuits and power.

### 4.4. Limitations and ensuring user safety

One of the primary limitations of this work is the small sample size, consisting of only two clinical case studies. The clinical case studies presented in this report are proof-of-concept feasibility tests, not designed to evaluate efficacy. While these cases offer preliminary insights into the feasibility of using OpenXstim for tSCS, they do not allow for generalization of outcomes or statistical significance. A controlled clinical study involving large sample size is necessary to evaluate the effectiveness of the spinal cord neuromodulation intervention delivered by OpenXstim across diverse populations and injury profiles.
An important limitation of this report is the use of different outcome assessment tools across the two case studies. While the ISNCSCI is the goldstandard measure for assessing sensory and motor recovery following SCI, the MAS was used in Case 2 to evaluate functional performance. The MAS

Table 3. Bill of materials (BOM) of OpenXstim with itemized cost in US dollars.

No. | Item name | Description | Unit price | Units | Subtotal
1 | A1 | Arduino UNO | 20.64 | 1 | 20.64
2 | BZ1 | Buzzer | 0.82 | 1 | 0.82
3 | C1–C5 | 10 uF | 0.24 | 5 | 1.2
4 | C8 | 22 uF | 0.75 | 1 | 0.75
5 | C6, C7, C10–C14 | 100 n | 0.24 | 7 | 1.68
6 | D0 | LED | 0.27 | 1 | 0.27
7 | IC1, IC2 | OPA454 | 7.63 | 2 | 15.26
8 | R0 | 270 R | 0.16 | 1 | 0.16
9 | R2 | 100 R | 0.16 | 1 | 0.16
10 | R1, R3, R4, R19 | 10 K | 0.16 | 4 | 0.64
11 | R6, R7, R9–R11, R13 | 1 M | 0.16 | 6 | 0.96
12 | R5, R8 | ORNTA2502AT1 | 7.79 | 2 | 15.58
13 | R12, R15 | 49R9 | 0.16 | 2 | 0.32
14 | R14, R16 | 10 R | 0.16 | 2 | 0.32
15 | R17, R18 | 1 K | 0.16 | 2 | 0.32
16 | SW1 | PEC12R-4025F-S0024 | 2.75 | 1 | 2.75
17 | SW2 | SW_SPDT | 0.72 | 1 | 0.72
18 | U1 | ICL7660S | 2.27 | 1 | 2.27
19 | U2 | AD5722AREZ | 19.39 | 1 | 19.39
20 | U3 | AZ1117EH-5.0TRG1 | 0.75 | 1 | 0.75
21 | U5 | MDOB128032 | 12.61 | 1 | 12.61
22 | U6, U8 | NMT0572SC | 26.21 | 2 | 52.42
| | Total | | | US$149.99

was originally developed and validated for stroke rehabilitation; however, it has also been applied in individuals with SCI to evaluate sitting balance and functional transitions (Jørgensen et al 2011). Given that the participant in Case 2 primarily trained for sit-to-stand, dynamic trunk control, and gait tasks, MAS provided a sensitive measure of functional improvement that may not be captured by ISNCSCI motor scores (Tharu et al 2023). Nevertheless, the inconsistency in assessment tools limits the direct comparability between cases, and future studies should employ standardized and validated outcome measures specific to SCI rehabilitation.
Another key limitation is the absence of long-term safety data for the use of OpenXstim in chronic stimulation. Although short-term usage did not result in adverse effects in the current cases, prolonged or repeated exposure to electrical stimulation requires careful evaluation, especially given the potential for skin irritation, burns, or electrode-related complications. For additional safety, in our design, we used a DC blocking capacitor in each stimulation channel. This ensures stopping any prolonged constant voltage or current to be delivered to through the stimulation electrodes in the event of stimulator malfunction (van Dongen and Serdijn 2016). Additionally, to prevent risks such as uneven current distribution, burns, and electrode movement, it is essential to ensure that electrodes are securely and properly attached to the skin (Nussbaum et al 2017). Regularly inspect the gel for any signs of dryness or loss of adhesion, especially at the edges, and reapply as needed to maintain consistent contact. This helps to ensure proper conductivity and prevent the gel from lifting, which can lead to increased current density and other safety hazards.
In both case studies, managing electrical currents to prevent discomfort highlights the importance of controlling the intensity of stimulation. An additional feature that could be implemented to address this issue is the integration of current ramp-up/rampdown functionality, a standard feature in many electrical stimulation systems (Nussbaum et al 2017). This feature gradually increases or decreases the electrical current, allowing for a smoother transition in muscle activation and preventing abrupt changes that could cause discomfort or injury. Ramping up the current gradually ensures that the muscles and tissues can adapt to the stimulation, particularly in sensitive individuals or during long-term usage. Similarly, ramping down the current allows for a safe reduction in intensity, which can help prevent sudden muscle release, thus improving safety and comfort throughout the therapy.
The stimulator’s operability was also assessed during 30 min of continuous use, corresponding to the typical therapeutic session duration. Moderate heating was observed in the 5.0 V linear regulator (AZ117EH-5.0TRG1) and minimal heating in the DC–DC boost converter (NMT0572SC), indicating acceptable thermal performance. Future versions may eliminate the linear regulator by using a regulated 5 V power source to improve efficiency and reduce heat buildup.

### 4.5. Future enhancements and expanded

applications
The current OpenXstim firmware does not include real-time impedance monitoring, which is a standard feature in many clinical-grade stimulation devices. Continuous impedance monitoring is crucial for ensuring consistent and safe electrical delivery, especially in dynamic environments where electrode-skin contact may fluctuate due to movement, sweating, or drying of conductive gel (Vargas Luna et al 2015). Although our design utilizes a constant current source that dynamically adjusts its output current based on the variable load, the absence of real-time impedance monitoring may increase the risk of uneven current distribution, discomfort, or localized skin heating. Integrating impedance monitoring would not only enhance safety but also improve the precision of stimulation delivery and help prevent unintended fluctuations in current during therapy sessions. Our hardware design already includes circuitry— such as current sensing resistor and analog-to-digital converter—that enables load impedance measurement (see supplementary 1). However, this functionality has not yet been implemented in the firmware. Incorporating impedance monitoring into the firmware should be prioritized in future iterations of the device.
The calibration offset of the stimulation current is primarily due to small mismatches in the resistor network of the improved Howland current pump circuit. Despite using high-precision matched resistors, these mismatches—along with the influence of the current control resistor and the finite open-loop gain of the operational amplifier—can reduce output impedance and introduce load-dependent variations, especially at higher stimulation intensities (Ghorbani and Nahvi 2019). Future improvements may include tighter tolerance components and firmware-based closed-loop calibration to enhance accuracy and linearity.
Although the stimulator includes a power switch that can disconnect it is power anytime, adding an additional emergency stop switch would be beneficiary for the user. Additional features, such as wireless control and signal monitoring, can be easily incorporated to enhance the functionality and usability of the stimulator. Since the stimulator is an Arduino Uno shield, using an Uno board with wireless capabilities such as Minima or WiFi would allow it to function as a wireless stimulator. This modification would enable its use in extended applications, such as brain-computer interface control or electronic bypass of SCI, as we demonstrated previously (Alam et al 2014, Li et al 2014, McGeady et al 2022).

### 5. Conclusion

OpenXstim was designed using commercially available components to ensure global accessibility and ease of replication. Bench testing confirmed the device’s ability to deliver reliable high frequency burst stimulation, while preliminary clinical case studies demonstrated its potential to improve sensory and motor function in individuals with chronic paralysis. OpenXstim addresses a critical gap in the availability of accessible neuromodulation technologies— particularly for use in low-resource settings. Its open-source design, including hardware schematics, firmware, and documentation, is freely available (https://github.com/OpenMedTech-Lab/OpenXstim) to support reproducibility and customization. OpenXstim represents a promising step toward democratizing spinal cord stimulation therapy and expanding global research capacity in neuromuscular rehabilitation.

Data availability statement

Design source files and additional documentation related to the OpenXstim stimulator are available in the online public repository: https://github.com/OpenMedTech-Lab/OpenXstim (https://github.com/OpenMedTech-Lab/OpenXstim)
Technical data set of OpenXstim v1.0 available at https://doi.org/10.1088/1741-2552/ae20c2/data1.

Acknowledgment

We sincerely thank the study participants for their time, valuable feedback, and contribution to the evaluation of the OpenXstim stimulator.

Conflict of interest

The authors declare no competing interests.

Funding

The authors did not receive any funding for this work.

Authors’ contributions

M.A. wrote the main manuscript text with parts from V.N., M.A.R. and V.A. N.N., F.T. and M.S.I helped with the case studies. P.T. and M.S.H. examined and validated the clinical data. A.M. revised and corrected the main manuscript and provided inputs to improve the manuscript. All authors reviewed the final manuscript.

Consent for publication

Informed consent for publication of anonymized data and results was obtained from all the study participants.

Disclaimers

The stimulator design is provided as-is and, despite careful development and extensive testing, no warranties are offered regarding its performance or safety. The authors cannot be held liable for any accidents or misuse of the stimulator.

Ethics approval and consent to participate

The studies involving human participants were conducted in accordance with the ethical standards and with the 1964 Helsinki Declaration and its later amendments. Ethical approvals were obtained for both case studies.

Users’ safety notes

- The design is intended exclusively for research and educational purposes.
- The stimulator has not been approved for use on humans or animals without prior authorization from a relevant ethics committee, such as an Institutional Review Board.
- The stimulator can produce high voltage. It must never be positioned across the chest, head, or in close proximity to the heart.
- The stimulator should never be powered through an external adapter, USB, or any other power source while in use or when connected to the body.
- Stimulation electrodes should be securely attached to the skin, and the gel remains intact to prevent uneven current distribution, and the risk of skin irritation or burns.

License

All the source files of the stimulator are licensed under the Creative Commons Attribution Share Alike 4.0 International License.

ORCID iDs

Monzurul Alam (https://orcid.org/0000-0003-0987-1999) 0000-0003-0987-1999 (https://orcid.org/0000-0003-0987-1999) Md Shofiqul Islam (https://orcid.org/0000-0001-8085-7976) 0000-0001-8085-7976 (https://orcid.org/0000-0001-8085-7976) Mohammad Sohrab Hossain
0000-0002-8452-1641 (https://orcid.org/0000-0002-8452-1641)
Alistair McEwan (https://orcid.org/0000-0001-7597-6372) 0000-0001-7597-6372 (https://orcid.org/0000-0001-7597-6372)

References

Alam M 2022 An easy-to-build transcutaneous electrical stimulator for spinal cord stimulation therapy
Alam M, Chen X, Zhang Z, Li Y and He J 2014 A brain-machine-muscle interface for restoring hindlimb locomotion after complete spinal transection in rats PLoS One 9 (https://doi.org/10.1371/journal.pone.0103764) e103764 (https://doi.org/10.1371/journal.pone.0103764)
Alam M, Ling Y T, Rahman M A, Wong A Y L, Zhong H, Edgerton V R and Zheng Y-P 2023 Restoration of over-ground walking via non-invasive neuromodulation therapy: a single-case study J. Clin. Med. 12 (https://doi.org/10.3390/jcm12237362) 7362 (https://doi.org/10.3390/jcm12237362)

Alam M, Ling Y T, Wong A Y L, Zhong H, Edgerton V R and Zheng Y-P 2020 Reversing 21 years of chronic paralysis via non-invasive spinal cord neuromodulation: a case study Ann. Clin. Transl. Neurol. 7 (https://doi.org/10.1002/acn3.51051) 829–38 (https://doi.org/10.1002/acn3.51051)
Alashram A R et al 2021 Transcutaneous spinal cord stimulation effects on spasticity in patients with spinal cord
injury: a systematic review J. Spinal Cord Med.
46 (https://doi.org/10.1080/10790268.2021.2000200) 1–8 (https://doi.org/10.1080/10790268.2021.2000200)
Bryson N, Lombardi L, Hawthorn R, Fei J, Keesey R, Peiffer J D and Seánez I 2023 Enhanced selectivity of transcutaneous ˜ spinal cord stimulation by multielectrode configuration J. Neural Eng. 20 (https://doi.org/10.1088/1741-2552/ace552) 046015 (https://doi.org/10.1088/1741-2552/ace552)
Calderone A, Cardile D, Gangemi A, De Luca R, Quartarone A, Corallo F and Calabr`o R S 2024 Traumatic brain injury and neuromodulation techniques in rehabilitation: a scoping review Biomedicines 12 (https://doi.org/10.3390/biomedicines12020438) 438 (https://doi.org/10.3390/biomedicines12020438)
Calvert J S, Manson G A, Grahn P J and Sayenko D G 2019 Preferential activation of spinal sensorimotor networks via lateralized transcutaneous spinal stimulation in neurologically intact humans J. Neurophysiol.
122 (https://doi.org/10.1152/jn.00454.2019) 2111–8 (https://doi.org/10.1152/jn.00454.2019)
Coelho-Magalh˜aes T, Fachin-Martins E, Silva A, Azevedo Coste C and Resende-Martins H 2022 Development of a high-power capacity open source electrical stimulation system to enhance research into FES-assisted devices: validation of FES cycling Sensors 22 (https://doi.org/10.3390/s22020531) 531 (https://doi.org/10.3390/s22020531)
Comino-Suárez N, Moreno J C, Megía-García A, Del-ama A J, ´
Serrano-Munoz D, Avenda ˜ | no-Coy J, Gil-Agudo ˜ | A, ´
Alcobendas-Maestro M, López-López E and Gómez-Soriano J 2025 Transcutaneous spinal cord stimulation combined with robotic-assisted body weight-supported treadmill training enhances motor score and gait recovery in incomplete spinal cord injury: a double-blind randomized controlled clinical trial J. Neuroeng. Rehabil. 22 (https://doi.org/10.1186/s12984-025-01545-8) 15 (https://doi.org/10.1186/s12984-025-01545-8)
Dalrymple A N, Hooper C A, Kuriakose M G, Capogrosso M and Weber D J 2023 Using a high-frequency carrier does not improve comfort of transcutaneous spinal cord stimulation
J. Neural Eng. 20 (https://doi.org/10.1088/1741-2552/acabe8) 016016 (https://doi.org/10.1088/1741-2552/acabe8)
Estes S, Zarkou A, Hope J M, Suri C and Field-Fote E C 2021 Combined transcutaneous spinal stimulation and locomotor training to improve walking function and reduce spasticity in subacute spinal cord injury: a randomized study of clinical feasibility and efficacy J. Clin. Med.
10 (https://doi.org/10.3390/jcm10061167) 1167 (https://doi.org/10.3390/jcm10061167)
Gad P, Hastings S, Zhong H, Seth G, Kandhari S and
Edgerton V R 2021 Transcutaneous spinal neuromodulation reorganizes neural networks in patients with cerebral palsy Neurotherapeutics 18 (https://doi.org/10.1007/s13311-021-01087-6) 1953–62 (https://doi.org/10.1007/s13311-021-01087-6)
Gelenitis K et al 2025 Non-invasive transcutaneous spinal cord stimulation programming recommendations for the treatment of upper extremity impairment in tetraplegia Neuromodulation 28 (https://doi.org/10.1016/j.neurom.2024.05.005) 162–73 (https://doi.org/10.1016/j.neurom.2024.05.005)
Gerasimenko Y, Gorodnichev R, Moshonkina T, Sayenko D, Gad P and Reggie Edgerton V 2015 Transcutaneous electrical spinal-cord stimulation in humans Ann. Phys. Rehabil. Med. 58 (https://doi.org/10.1016/j.rehab.2015.05.003) 225–31 (https://doi.org/10.1016/j.rehab.2015.05.003)
Ghorbani R and Nahvi M 2019 Analysis of performance of Howland AC current source for electrical impedance spectro-tomography Sens. Imaging 20 (https://doi.org/10.1007/s11220-019-0251-1) 28 (https://doi.org/10.1007/s11220-019-0251-1)
Gopaul U, Bayley M T and Kalsi-Ryan S 2025 Combined activity-based therapy and cervical spinal cord stimulation: active ingredients, targets and mechanisms of actions to optimize neurorestoration of upper limb function after cervical spinal cord injury Physiother. Res. Int.
30 (https://doi.org/10.1002/pri.70036) e70036 (https://doi.org/10.1002/pri.70036)
Gordineer E A, Stokic D S and Krenn M J 2024 Distinguishing reflex from non-reflex responses elicited by transcutaneous spinal stimulation targeting the lumbosacral cord in healthy individuals Exp. Brain Res. 242 (https://doi.org/10.1007/s00221-024-06790-2) 959–70 (https://doi.org/10.1007/s00221-024-06790-2)
Grishin A A, Moshonkina T R, Bobrova E V and Gerasimenko Y P 2019 A device for the rehabilitation therapy of patients with motor pathology using mechanotherapy, transcutaneous electrical stimulation of the spinal cord, and biological feedback Biomed. Eng. 53 (https://doi.org/10.1007/s10527-019-09914-z) 227–30 (https://doi.org/10.1007/s10527-019-09914-z)
Hastings S, Zhong H, Feinstein R, Zelczer G, Mitrovich C, Gad P and Edgerton V R 2022 A pilot study combining noninvasive spinal neuromodulation and activity-based neurorehabilitation therapy in children with cerebral palsy Nat. Commun. 13 (https://doi.org/10.1038/s41467-022-33208-w) 5660 (https://doi.org/10.1038/s41467-022-33208-w)
Hofstoetter U S, Freundl B, Binder H and Minassian K 2018 Common neural structures activated by epidural and transcutaneous lumbar spinal cord stimulation: elicitation of posterior root-muscle reflexes PLoS One 13 (https://doi.org/10.1371/journal.pone.0192013) e0192013 (https://doi.org/10.1371/journal.pone.0192013) Hofstoetter U S, Freundl B, Danner S M, Krenn M J, Mayr W, Binder H and Minassian K 2020 Transcutaneous spinal cord stimulation induces temporary attenuation of spasticity in individuals with spinal cord injury J. Neurotrauma
37 (https://doi.org/10.1089/neu.2019.6588) 481–93 (https://doi.org/10.1089/neu.2019.6588)
Hofstoetter U S, Freundl B, Lackner P and Binder H 2021 Transcutaneous spinal cord stimulation enhances walking performance and reduces spasticity in individuals with multiple sclerosis Brain Sci. 11 (https://doi.org/10.3390/brainsci11040472) 472 (https://doi.org/10.3390/brainsci11040472)
Hofstoetter U S and Minassian K 2022 Transcutaneous spinal cord stimulation: advances in an emerging non-invasive strategy for neuromodulation J. Clin. Med. 11 (https://doi.org/10.3390/jcm11133836) 3836 (https://doi.org/10.3390/jcm11133836) Jørgensen V, Elfving B and Opheim A 2011 Assessment of unsupported sitting in patients with spinal cord injury Spinal Cord 49 (https://doi.org/10.1038/sc.2011.9) 838–43 (https://doi.org/10.1038/sc.2011.9)
Krenn M J, White J M, Stokic D S and Tansey K E 2023 Neuromodulation with transcutaneous spinal stimulation reveals different groups of motor profiles during robot-guided stepping in humans with incomplete spinal cord injury Exp. Brain Res. 241 (https://doi.org/10.1007/s00221-022-06521-5) 365–82 (https://doi.org/10.1007/s00221-022-06521-5)
Kreydin E I et al 2024 A pilot study of the effect of transcutaneous spinal cord stimulation on micturition-related brain activity and lower urinary tract symptoms after stroke J. Urol.
211 (https://doi.org/10.1097/JU.0000000000003776) 294–304 (https://doi.org/10.1097/JU.0000000000003776)
Kreydin E, Zhong H, Lavrov I, Edgerton V R and Gad P 2022 The effect of non-invasive spinal cord stimulation on anorectal function in individuals with spinal cord injury: a case series Front. Neurosci. 16 (https://doi.org/10.3389/fnins.2022.816106) 816106 (https://doi.org/10.3389/fnins.2022.816106)
Leal Filho W et al 2022 An assessment of requirements in investments, new technologies, and infrastructures to achieve the SDGs Environ. Sci. Eur. 34 (https://doi.org/10.1186/s12302-022-00629-9) 58 (https://doi.org/10.1186/s12302-022-00629-9)
Li Y, Alam M, Guo S, Ting K H and He J 2014 Electronic bypass of spinal lesions: activation of lower motor neurons directly driven by cortical neural signals J. Neuroeng. Rehabil. 11 (https://doi.org/10.1186/1743-0003-11-107) 107 (https://doi.org/10.1186/1743-0003-11-107) Lucas K et al 2025 Non-invasive spinal neuromodulation enables stepping in children with complete spinal cord injury Brain148 (https://doi.org/10.1093/brain/awaf115) 3290–99 (https://doi.org/10.1093/brain/awaf115)
Manson G A, Calvert J S, Ling J, Tychhon B, Ali A and
Sayenko D G 2020 The relationship between maximum tolerance and motor activation during transcutaneous spinal stimulation is unaffected by the carrier frequency or vibration Physiol. Rep. 8 (https://doi.org/10.14814/phy2.14397) e14397 (https://doi.org/10.14814/phy2.14397)
Martin R 2021 Utility and feasibility of transcutaneous spinal cord stimulation for patients with incomplete SCI in therapeutic settings: a review of topic Front. Rehabil. Sci. 2 (https://doi.org/10.3389/fresc.2021.724003) 724003 (https://doi.org/10.3389/fresc.2021.724003) McGeady C, Vucˇkovi´c A, Singh Tharu N, Zheng Y-P and Alam M 2022 Brain-computer interface priming for cervical transcutaneous spinal cord stimulation therapy: an exploratory case study Front. Rehabil. Sci. 3 (https://doi.org/10.3389/fresc.2022.896766) 896766 (https://doi.org/10.3389/fresc.2022.896766)
Merrill D R, Bikson M and Jefferys J G R 2005 Electrical stimulation of excitable tissue: design of efficacious and safe protocols J. Neurosci. Methods 141 (https://doi.org/10.1016/j.jneumeth.2004.10.020) 171–98 (https://doi.org/10.1016/j.jneumeth.2004.10.020)
Minassian K, Freundl B, Lackner P and Hofstoetter U S 2024 Transcutaneous spinal cord stimulation neuromodulates pre- and postsynaptic inhibition in the control of spinal spasticity Cell Rep. Med. 5 (https://doi.org/10.1016/j.xcrm.2024.101805) 101805 (https://doi.org/10.1016/j.xcrm.2024.101805)
Minassian K, Hofstoetter U S, Danner S M, Mayr W, Bruce J A, McKay W B and Tansey K E 2016 Spinal rhythm generation by step-induced feedback and transcutaneous posterior root stimulation in complete spinal cord-injured individuals Neurorehabil. Neural Repair. 30 (https://doi.org/10.1177/1545968315591706) 233–43 (https://doi.org/10.1177/1545968315591706)
Moon Y et al 2024 Noninvasive spinal stimulation improves walking in chronic stroke survivors: a proof-of-concept case series Biomed. Eng. Online 23 (https://doi.org/10.1186/s12938-024-01231-1) 38 (https://doi.org/10.1186/s12938-024-01231-1)
Moritz C et al 2024 Non-invasive spinal cord electrical stimulation for arm and hand function in chronic tetraplegia: a safety and efficacy trial Nat. Med.
30 (https://doi.org/10.1038/s41591-024-02940-9) 1276–83 (https://doi.org/10.1038/s41591-024-02940-9)
Moshonkina T R, Zharova E, Ananev S, Shandybina N, Vershinina E, Lyakhovetskii V, Grishin A, Shlyakhto E and Gerasimenko Y 2022 A new technology for recovery of locomotion in patients after a stroke Dokl. Biochem. Biophys. 507 (https://doi.org/10.1134/S1607672922340087) 353–6 (https://doi.org/10.1134/S1607672922340087)
Nuechterlein A, Feng L, Yehia A and Illes J 2023 Strengths, gaps, and future directions on the landscape of ethics-related research for spinal cord injury Spinal Cord 61 (https://doi.org/10.1038/s41393-023-00897-z) 477–82 (https://doi.org/10.1038/s41393-023-00897-z) Nussbaum E L, Houghton P, Anthony J, Rennie S, Shay B L and Hoens A M 2017 Neuromuscular electrical stimulation for treatment of muscle impairment: critical review and recommendations for clinical practice Physiother. Can. 69 (https://doi.org/10.3138/ptc.2015-88) 1–76 (https://doi.org/10.3138/ptc.2015-88)
Parhizi B, Barss T S and Mushahwar V K 2021 Simultaneous cervical and lumbar spinal cord stimulation induces facilitation of both spinal and corticospinal circuitry in humans Front. Neurosci. 15 (https://doi.org/10.3389/fnins.2021.615103) 615103 (https://doi.org/10.3389/fnins.2021.615103)
Qian Q et al 2020 Restoration of arm and hand functions via noninvasive cervical cord neuromodulation after traumatic brain injury: a case study Brain Injury 34 (https://doi.org/10.1080/02699052.2020.1850864) 1–10 (https://doi.org/10.1080/02699052.2020.1850864)
Rahman M A, Tharu N S, Gustin S M, Zheng Y-P and Alam M 2022 Trans-spinal electrical stimulation therapy for functional rehabilitation after spinal cord injury: review J. Clin. Med. 11 (https://doi.org/10.3390/jcm11061550) 1550 (https://doi.org/10.3390/jcm11061550)
Sachdeva R, Girshin K, Shirkhani Y and Gad P 2024 Beyond pediatrics: noninvasive spinal neuromodulation improves motor function in an adult with cerebral palsy Bioelectron. Med. 10 (https://doi.org/10.1186/s42234-023-00133-2) 1 (https://doi.org/10.1186/s42234-023-00133-2)
Samejima S, Caskey C D, Inanici F, Shrivastav S R, Brighton L N, Pradarelli J, Martinez V, Steele K M, Saigal R and Moritz C T 2022 Multisite transcutaneous spinal stimulation for walking and autonomic recovery in motor-incomplete tetraplegia: a single-subject design Phys. Ther.
102 (https://doi.org/10.1093/ptj/pzab228) pzab228 (https://doi.org/10.1093/ptj/pzab228)
Santos S, Schlebusch T and Leonhardt S 2013 Simulation of a current source with a Cole-Cole load for multi-frequency electrical impedance tomography Annual Int. Conf. IEEE Engineering in Medicine and Biology Society pp 6445–8 Sayenko D G, Atkinson D A, Dy C J, Gurley K M, Smith V L, Angeli C, Harkema S J, Edgerton V R and Gerasimenko Y P 2015 Spinal segment-specific transcutaneous stimulation differentially shapes activation pattern among motor pools in humans J. Appl. Physiol. 118 (https://doi.org/10.1152/japplphysiol.01128.2014) 1364–74 (https://doi.org/10.1152/japplphysiol.01128.2014)
Shamantseva N, Timofeeva O, Semenova V, Andreeva I and Moshonkina T 2024 Transcutaneous spinal cord stimulation modulates quiet standing in healthy adults: stimulation site and cognitive style matter Front. Neurosci.
18 (https://doi.org/10.3389/fnins.2024.1467182) 1467182 (https://doi.org/10.3389/fnins.2024.1467182)
Suggitt J, Symonds J and D’Amico J M 2025 Safety and effectiveness of multisite transcutaneous spinal cord stimulation combined with activity-based therapy when delivered in a community rehabilitation setting: a real-world pilot studySafety and effectiveness of multisite transcutaneous spinal cord stimulation combined with activity-based therapy when delivered in a community rehabilitation setting: a real-world pilot study Neuromodulation 28 (https://doi.org/10.1016/j.neurom.2025.01.005) 1144–56 (https://doi.org/10.1016/j.neurom.2025.01.005)
Tefertiller C, Rozwod M, VandeGriend E, Bartelt P, Sevigny M and Smith AC 2022 Transcutaneous electrical spinal cord stimulation to promote recovery in chronic spinal cord injury Front. Rehabil. Sci. 2 (https://doi.org/10.3389/fresc.2021.740307) 740307 (https://doi.org/10.3389/fresc.2021.740307)
Tharu N S, Alam M, Ling Y T, Wong A Y and Zheng Y-P 2023 Combined transcutaneous electrical spinal cord stimulation and task-specific rehabilitation improves trunk and sitting functions in people with chronic tetraplegia Biomedicines 11 (https://doi.org/10.3390/biomedicines11010034) 34 (https://doi.org/10.3390/biomedicines11010034)
Trout M A, Harrison A T, Brinton M R and George J A 2023 A portable, programmable, multichannel stimulator with high compliance voltage for noninvasive neural stimulation of motor and sensory nerves in humans Sci. Rep.
13 (https://doi.org/10.1038/s41598-023-30545-8) 3469 (https://doi.org/10.1038/s41598-023-30545-8)
Valtin M, Kociemba K, Behling C, Kuberski B, Becker S and Schauer T 2016 RehaMovePro: a versatile mobile stimulation system for transcutaneous FES applications Eur.
J. Trans. Myol. 26 (https://doi.org/10.4081/ejtm.2016.6076) 6076 (https://doi.org/10.4081/ejtm.2016.6076)
van Dongen M N and Serdijn W A 2016 Does a coupling capacitor enhance the charge balance during neural stimulation? An empirical study Med. Biol. Eng. Comput. 54 (https://doi.org/10.1007/s11517-015-1312-9) 93–101 (https://doi.org/10.1007/s11517-015-1312-9)
Vargas Luna J L, Krenn M, Cortés Ramírez J A and Mayr W 2015 Dynamic impedance model of the skin-electrode interface for transcutaneous electrical stimulation PLoS One
10 (https://doi.org/10.1371/journal.pone.0125609) e0125609 (https://doi.org/10.1371/journal.pone.0125609)
Zhang J, Wang M, Alam M, Zheng Y-P, Ye F and Hu X 2024 Effects of non-invasive cervical spinal cord
neuromodulation by trans-spinal electrical stimulation on cortico-muscular descending patterns in upper extremity of chronic stroke Front. Bioeng. Biotechnol. 12 (https://doi.org/10.3389/fbioe.2024.1372158) 1372158 (https://doi.org/10.3389/fbioe.2024.1372158)

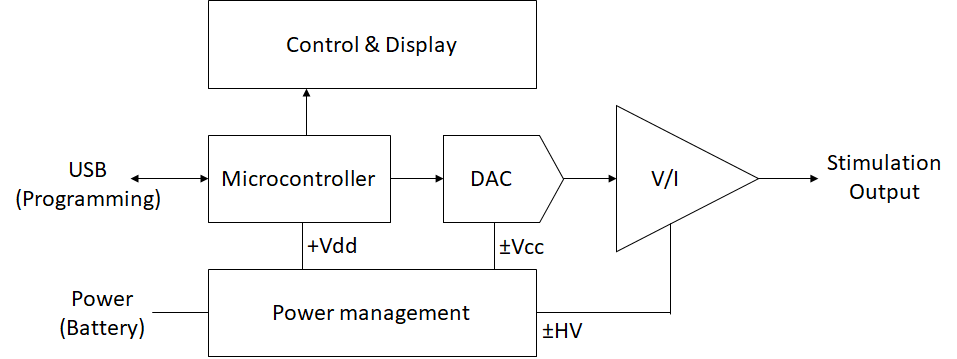
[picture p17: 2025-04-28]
BlockDiagram.png

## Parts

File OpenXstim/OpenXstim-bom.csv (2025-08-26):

Comment | Designator | Footprint
Buzzer | BZ1 | Buzzer_Beeper:Buzzer_12x9.5RM7.6
10uF | C2, C3 | Capacitor_SMD:CP_Elec_5x5.3
10uF | C1, C5 | Capacitor_SMD:C_1206_3216Metric
22uF | C8 | Capacitor_SMD:CP_Elec_5x5.4
10uF | C4, C9 | Capacitor_SMD:CP_Elec_8x10.5
100n | C6, C7, C10, C11, C12, C13, C14 | Capacitor_SMD:C_0805_2012Metric
0.1uF | C15, C16 | Capacitor_SMD:C_0805_2012Metric
LED | D0 | LED_SMD:LED_1206_3216Metric
OPA454 | IC1, IC2 | RehabExo:SO08GP
Test_2 | J1 | Connector_PinHeader_2.54mm:PinHeader_1x02_P2.54mm_Vertical
MJ-2506N | J2, J3 | RehabExo:CUI_MJ-2506N
Test_1 | J4 | Connector_PinHeader_2.54mm:PinHeader_1x02_P2.54mm_Vertical
Ref | J5 | Connector_PinHeader_2.54mm:PinHeader_1x02_P2.54mm_Vertical
Trigger | J6 | Connector_PinHeader_2.54mm:PinHeader_1x02_P2.54mm_Vertical
270R | R0 | Resistor_SMD:R_0805_2012Metric
100R | R2 | Resistor_SMD:R_0805_2012Metric
10K | R1, R3, R4, R19 | Resistor_SMD:R_0805_2012Metric
ORNTA2502AT1 | R5, R8 | RehabExo:ORN_VIS
100K | R6, R7 | Resistor_SMD:R_0805_2012Metric
1M | R9, R10, R11, R13 | Resistor_SMD:R_0805_2012Metric
49R9 | R12, R15 | Resistor_SMD:R_0805_2012Metric
10R | R14, R16 | Resistor_SMD:R_0805_2012Metric
1K | R17, R18 | Resistor_SMD:R_0805_2012Metric
PEC12R-4025F-S0024 | SW1 | RehabExo:ENC_PEC12R-4025F-S0024
SW_SPDT | SW2 | RehabExo:SW_MINI-SPDT-SW
LT1054 | U1 | Package_SO:SOIC-8_3.9x4.9mm_P1.27mm
AD5722AREZ | U2 | RehabExo:RE_24_ADI
AZ1117EH-5.0TRG1 | U3 | Package_TO_SOT_SMD:SOT-223
MDOB128032 | U5 | RehabExo:MDOB128032GV-WI
NMT0572SC | U6, U8 | RehabExo:NMT0572SC

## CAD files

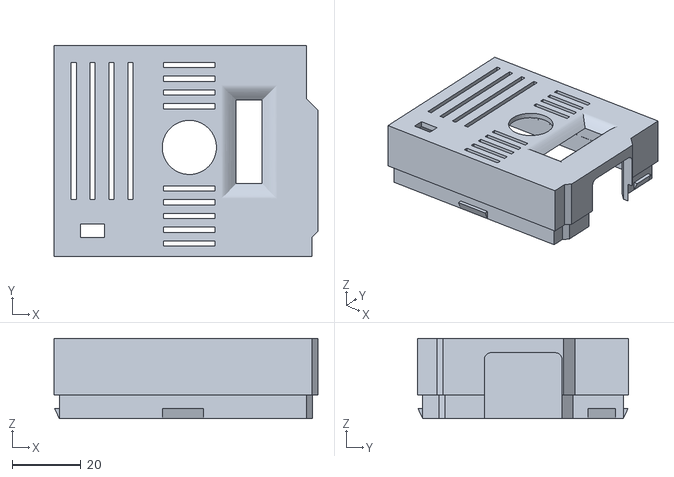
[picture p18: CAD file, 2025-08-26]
OpenXstim/Housing/OpenExostimV2_Top.STL
77.0 x 61.6 x 23.4

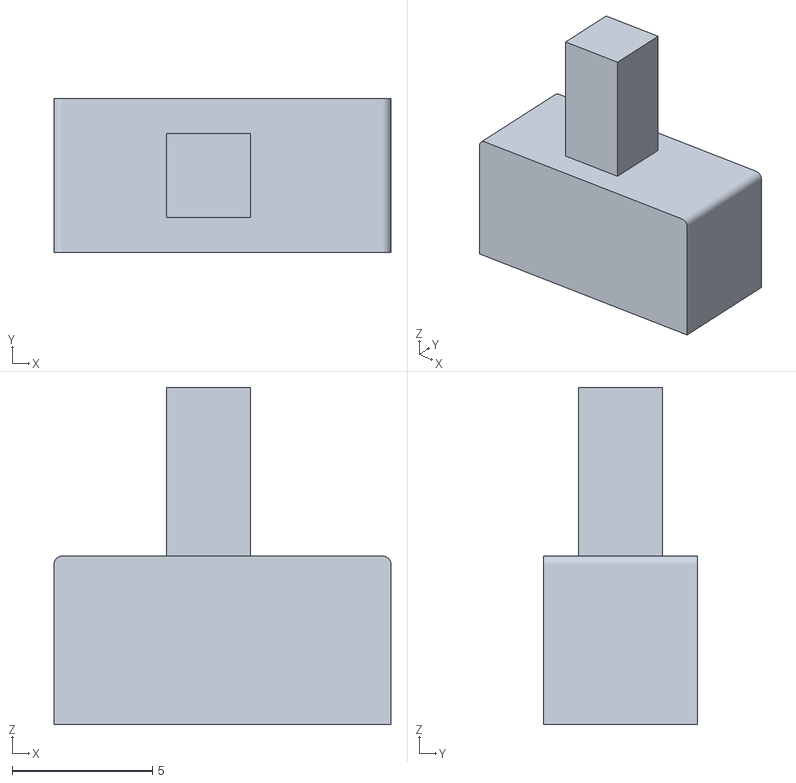
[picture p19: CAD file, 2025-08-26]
OpenXstim/Housing/OpenExoStimV2_Switch.STL
12.0 x 5.50 x 12.0

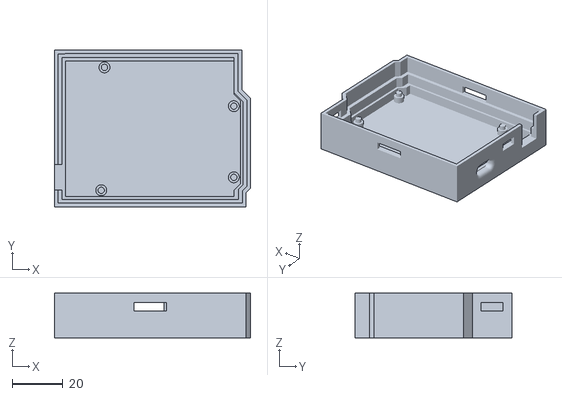
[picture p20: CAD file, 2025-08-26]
OpenXstim/Housing/OpenExoStimV2_Base.STL
77.0 x 61.6 x 17.5

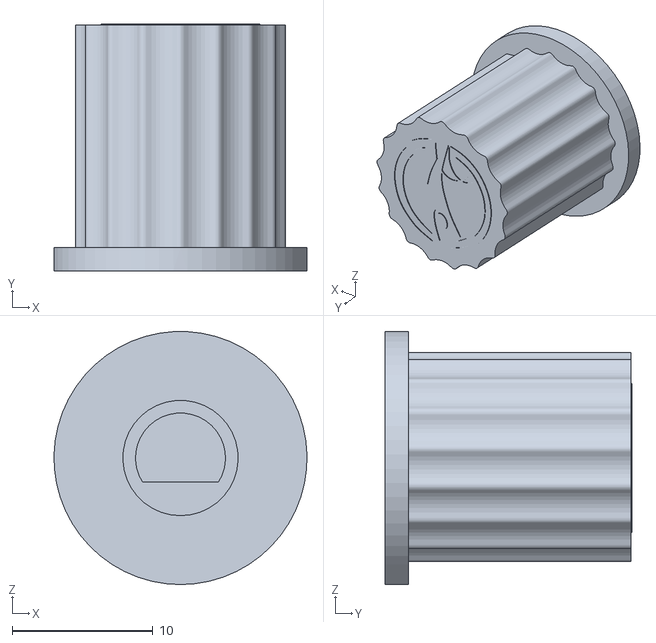
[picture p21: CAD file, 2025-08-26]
OpenXstim/Housing/OpenExoStim_Nob.STL
18.0 x 17.6 x 18.0

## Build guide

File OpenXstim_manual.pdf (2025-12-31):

## OpenXstim v1.0

# __________________________________________________

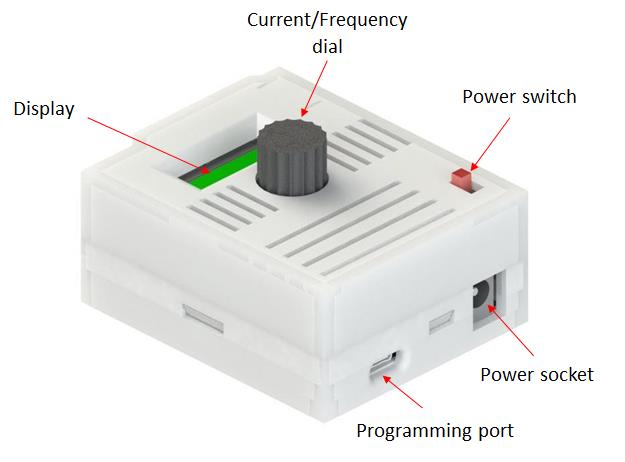
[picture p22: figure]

P a g e 1 | 10

Reference Manual

Description

OpenXstim is a dual-channel programmable constant current stimulator for transcutaneous electrical stimulation. The stimulator is capable of delivering up to 100 mA of biphasic current at a maximum of 10kHz stimulation frequency for each stimulation channel simultaneously. The stimulator board is designed as a popular Arduino Uno shield (recommended to use Arduino uno r4 minima) with pin-to-pin capability for easy programming and operation. An on-board rotary encoder also allows manual control of the stimulation intensity. The stimulation current is automatically sensed by the microcontroller and displayed on an on-board display.

Specifications

- Dimensions: 6.86 cm x 5.33 cm (Arduino Uno Shield)
- Current intensity: 0 – 110 mA (per channel)
- Compliance voltage: ±48 volt
- Stimulation frequency: up-to 10kHz
- Compatibility: Arduino Uno
- Idle bias current: 50 mA
- Full-load supply current: 260 mA
- Supply voltage: 6 – 12 volts DC (preferred: 9V 650 mAh battery)

Warnings

This device is intended for EDUCATION AND RESEARCH PURPOSES ONLY. It is not approved by any regulatory authority for medical or other uses. The user assumes all responsibility for injury or damage due to the misuse of this device.

Design

# __________________________________________________

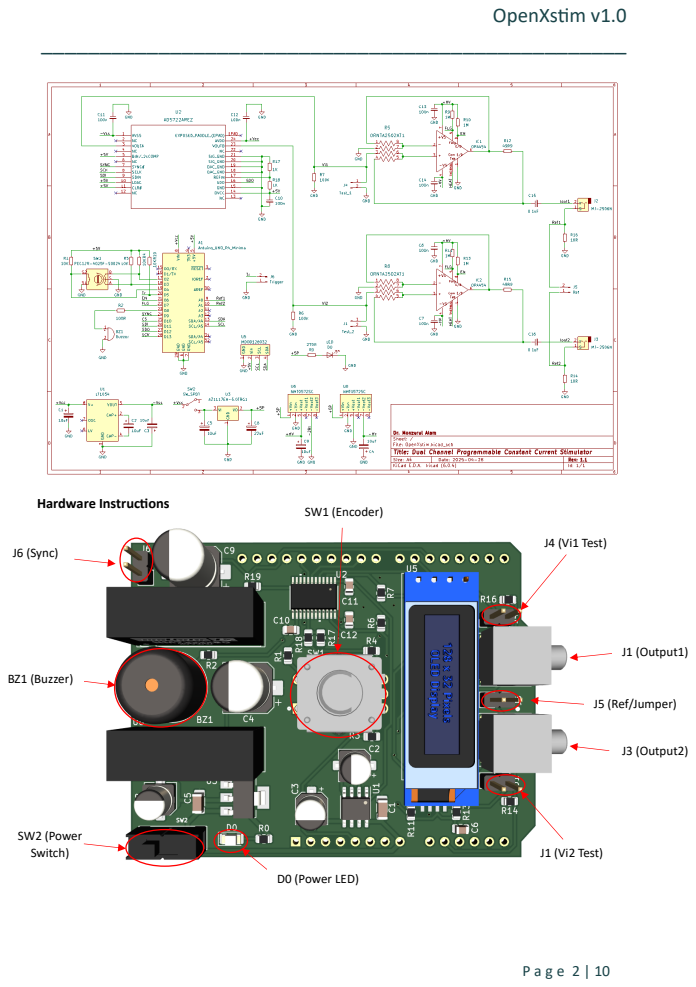
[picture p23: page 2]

# __________________________________________________

P a g e 3 | 10

J6 (Trigger): 2-pin connector to trigger the stimulator from external TTL pulse. The trigger pin is connected to Arduino Uno’s GPIO port D5 (pin 20). One must write an associative code to enable the D5 port pin as an input mode to allow the trigger to Sync the stimulation output. Please ignore this port pin if you are not using external trigger.

BZ1 (Buzzer): Built-in active buzzer connected to Arduino Uno’s GPIO port D8 (pin 23) though a resistor. A logic HIGH to this pin will generate a sound. One should write an associative code to enable the D8 port pin as an output mode to allow to generate the sound.

SW2 (Power): Sliding switch to power the ±HV circuit. It draws power through Arduino Uno’s VIN pin. Please connect a 7-12 volts DC power supply (preferably 9V 650 mAh battery) to the barrel plug (not shown in the picture). To save power, turn ON the SW2 switch (slide outward of the board) only prior to stimulation. The adjacent red LED (D0) glows when the switch is ON.

J4-J1 (Test points): These points provide the voltage operation of the stimulator. To examine the operation of the stimulator, connect an oscilloscope probe to these connectors, positive to the right (pin 1) and ground to left (pin 2).

SW1 (Encoder): Rotate this to increase and decease the stimulation intensity. The Encoder also incorporates a push switch to allow additional programming option such as selecting or resetting values. The pulled-up switch is connected to the microcontroller’s GPIO pin D3 (pin 18).

D0 (LED): The LED allows additional programming option such as blinking during stimulation to allow visual status of the stimulator operation. The LED is connected to the microcontroller’s GPIO port D12 (pin 27) through a 270Ω resistor.

J5 (Ref/Jumper): This is a dual-purpose connector. The two pins of this connector is equipped with two 10Ω current sense resistors from the output terminals. The voltage drop across the resistor are fed to the analogue pins A0 & A1 (pin 9 & 10) of the Arduino uno microcontroller. An appropriate code should be written to allow the measurement of the sensed current through this ADC pins. Please note that the ADC can only read the positive part of the stimulation pulse. Alternatively, Once can connect an oscilloscope to this connector pins to measure the voltage drop across the current sense resistor to calculate the current value though the load. The 2nd operation of this connector is to utilize a jumper to allow a common reference point for the two-channel stimulation. This is particularly useful for brain or spinal cord stimulation where stimulation is provided across a common reference point.

J2-J3 (Outputs): These are 3.5 mm mono sockets to connect conventional TENS or EMS cables (see the following figure) for two channel stimulation output.

# __________________________________________________

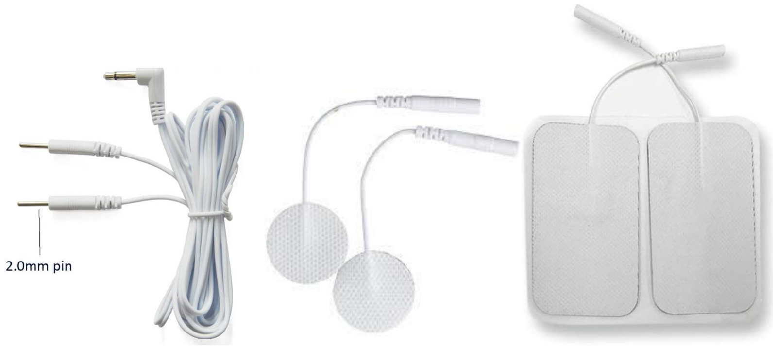
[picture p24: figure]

P a g e 4 | 10

Assembly

Example image (for reference only): Typical TENS/EMS cable of 2.5 mm mono connector and pairs of TENS/EMS electrodes with 2.0 mm female connector.

[Please use high power (> 650 mAh) battery to have better operation of OpenXstim]

# __________________________________________________

P a g e 5 | 10

APPENDIX 1: Arduino uno example open-source code for OpenXstim2 v1.0

/*********************************************************************** // 16 June 2023, Australia
// Example code for setting up stimulation current for OpenXatim2 v1.0 // For queries please email Dr Monzurul Alam at md.malam@connect.polyu.hk ***********************************************************************/

#include <Wire.h>

#include <Adafruit_GFX.h>

#include <Adafruit_SSD1306.h> #include <stdint.h>

#include <AD57.h>

// set your stimulation parameters
#define Hz 20 | // stimulation frequency

#define pulse_number 10 | // number of pulses in a burst

#define pulse_width 50 // pulse width in microsecond int current = 0; // declare initial current intensity int calibration = 4; // set intensity calibration value

/****************************************************** * user variables
*****************************************************/ // MUST : select the kind of AD57xx you have:
// AD5722 or AD5732 or AD5752
uint8_t DacType = AD5722;

// MUST : select the DAC channel to use (DAC_A, DAC_B or DAC_AB) #define DAC_CHANNEL DAC_AB

/* MUST : define the output voltage range (for Bipolar use pnxxx)
* p5V | +5V
* p10V | +10V
* p108V | +10.8V
* pn5V | +/-5V
* pn10V | +/-10V
* pn108V | +/-10.8V
*/
#define output_range pn5V

// MUST : DEFINE THE SYNC PIN CONNECTION FOR AD57xx
/* The initialisation and pulling high and low is handled by the * library. The sketch only needs to define the right pin.
*/
char slave_pin_DAC = 9;

// Define the SS1306 display connected to I2C pins

# __________________________________________________

P a g e 6 | 10

#define SCREEN_WIDTH 128 // OLED display width, in pixels

#define SCREEN_HEIGHT 32 // OLED display height, in pixels

#define LED_BLINK 12 // LED to blink during stimulation

// Declaration for an SSD1306 display connected to I2C (SDA, SCL pins) Adafruit_SSD1306 display(SCREEN_WIDTH, SCREEN_HEIGHT, &Wire, -1);

// Define rotary encoder pins
#define ENC_A 3

#define ENC_B 2

int16_t initial_value;
int16_t baseline = 2048;
int16_t value = baseline;
unsigned int Intensity = 0; // stimulation intensity unsigned long _lastIncReadTime = micros(); unsigned long _lastDecReadTime = micros();
int _pauseLength = 2500;
int _fastIncrement = 1;
char buffer[64]; // buffer must be big enough to hold all the message

void setup() {
pinMode(LED_BLINK, OUTPUT);
// Set encoder pins and attach interrupts
pinMode(ENC_A, INPUT_PULLUP);
pinMode(ENC_B, INPUT_PULLUP); attachInterrupt(digitalPinToInterrupt(ENC_A), read_encoder, CHANGE); attachInterrupt(digitalPinToInterrupt(ENC_B), read_encoder, CHANGE);
// Start the serial monitor to show output
Serial.begin(115200);
if(!display.begin(SSD1306_SWITCHCAPVCC, 0x3C)) { // Address 0x3D for 128x64 Serial.println(F("SSD1306 allocation failed"));
for(;;);
}
//serialTrigger(F("Press any key to begin +5V to -5V Bi-polar constant loop output range mode"));
/* enable or disable debug information from the library
* 0 = disable (default.. no need to call)
* 1 = enable
*/
AD57.debug(0);
Serial.println(F("Starting DAC"));
// initialise the AD57xx and connections to and
// from the AD57xx
init_AD57xx();
// set max count depending on AD57xx : 12, 14 or 16 bits if (DacType == AD5752) initial_value = 0xffff;
else if (DacType == AD5732) initial_value = 0x3fff;

# __________________________________________________

P a g e 7 | 10

else if (DacType == AD5722) initial_value = 0x0fff;
}

//**Main program**//
void loop() {
value = baseline + Intensity;
// generate stimulation pulses
for (int i=0; i<pulse_number; i++) { // positive phase
AD57.setDac(DAC_CHANNEL, value); delayMicroseconds(pulse_width); // negetive phase
AD57.setDac(DAC_CHANNEL, -value); delayMicroseconds(pulse_width); }
// no pulses
AD57.setDac(DAC_CHANNEL, baseline); delayMicroseconds(pulse_width);
delay(1000/Hz); // stimulation delay
//digitalWrite(LED_BLINK, !digitalRead(LED_BLINK)); // toggle LED

// print the value to serial display
display.clearDisplay();
display.setTextSize(2);
display.setTextColor(WHITE);
display.setCursor(0, 0);
// Calcluate and display set current intesity value current = Intensity / calibration; sprintf(buffer, "Current = %d mA", current); display.println(buffer);
display.display();
//Intensity = Intensity + 1; // for debugging only }

//**Interrupt service routine**//
void read_encoder() {
// Encoder interrupt routine for both pins. Updates Intensity // if they are valid and have rotated a full indent

static uint8_t old_AB = 3; // Lookup table index
static int8_t encval = 0; // Encoder value
static const int8_t enc_states[] = {0,-1,1,0,1,0,0,-1,-1,0,0,1,0,1,-1,0}; // Lookup table

old_AB <<=2; // Remember previous state

if (digitalRead(ENC_A)) old_AB |= 0x02; // Add current state of pin A

# __________________________________________________

P a g e 8 | 10

if (digitalRead(ENC_B)) old_AB |= 0x01; // Add current state of pin B

encval += enc_states[( old_AB & 0x0f )];

// Update Intensity if encoder has rotated a full indent, that is at least 4 steps
if( encval > 3 ) { | // Four steps forward
int changevalue = 5;
if((micros() - _lastIncReadTime) < _pauseLength) { changevalue = _fastIncrement * changevalue;
}
_lastIncReadTime = micros();
Intensity = Intensity + changevalue; | // Update Intensity
encval = 0;
}
else if( encval < -3 ) { // Four steps backward
int changevalue = -5;
if((micros() - _lastDecReadTime) < _pauseLength) { changevalue = _fastIncrement * changevalue;
}
_lastDecReadTime = micros();
if (Intensity > 0){
Intensity = Intensity + changevalue; | // Update Intensity
}
else{
Intensity = 0;
}
encval = 0;
}
}

/* initialize the connection with the board and set the default values */ void init_AD57xx()
{
// set output voltage range in binary
// if you want to test 2scomp, see remark 1 in AD57.h, use // AD57.begin(DAC_CHANNEL, output_range, COMP2); AD57.begin(DAC_CHANNEL, output_range);

Serial.print("get range "); Serial.println(AD57.getRange(DAC_CHANNEL));

// enable therminal shutdown and overcurrent protection
// also stop CLR as, starting from 0v after OP_CLEAR op_code)
// this can be changed for full negative after clear with
// AD57.setControl(OP_INSTR,(SET_TSD_ENABLE |SET_CLAMP_ENABLE|SET_CLR_SET)); AD57.setControl(OP_INSTR,(SET_TSD_ENABLE |SET_CLAMP_ENABLE|STOP_CLR_SET));

# __________________________________________________

P a g e 9 | 10

// clear the DAC outputs
AD57.setControl(OP_CLEAR); }

bool check_status(bool disp)
{
uint16_t stat = AD57.getStatus(); bool ret = 0;

if (stat & stat_err_TO)
{
Serial.println(F("Therminal overheat shutdown")); ret = 1;
}

if (stat & stat_err_CA)
{
Serial.println(F("DAC - A overcurrent detected")); ret = 1;
}

if (stat & stat_err_CB)
{
Serial.println(F("DAC - B overcurrent detected")); ret = 1;
}

if (disp == 1)
{
Serial.println(F("Display settings\n"));

if (stat & stat_TS)
Serial.println(F("Therminal shutdown protection enabled")); else
Serial.println(F("Therminal shutdown protection disabled"));

if (stat & stat_CLR)
Serial.println(F("DAC output set to midscale or fully negative with OP_CLEAR command"));
else
Serial.println(F("DAC output set to 0V with OP_CLEAR command"));

if (stat & stat_CLAMP)
Serial.println(F("Overcurrent protection enabled"));
else
Serial.println(F("Overcurrent protection disabled"));

# __________________________________________________

P a g e 10 | 10

if (stat & stat_SDO) // you will never see this one :-) Serial.println(F("Serial data out disabled"));
else
Serial.println(F("Serial data out enabled"));

Serial.println();
}

return(ret);
}

/* serialTrigger prints a message, then waits for something * to come in from the serial port.
*/
void serialTrigger(String message)
{
Serial.println();
Serial.println(message);
Serial.println();

while (!Serial.available());

while (Serial.available()) Serial.read();
}

/* errorLoop loops forever.*/ void errorLoop()
{
// power-off both channels AD57.setPower(STOP_PUA|STOP_PUB);

Serial.print(F("Critical error, looping forever")); for (;;);
}

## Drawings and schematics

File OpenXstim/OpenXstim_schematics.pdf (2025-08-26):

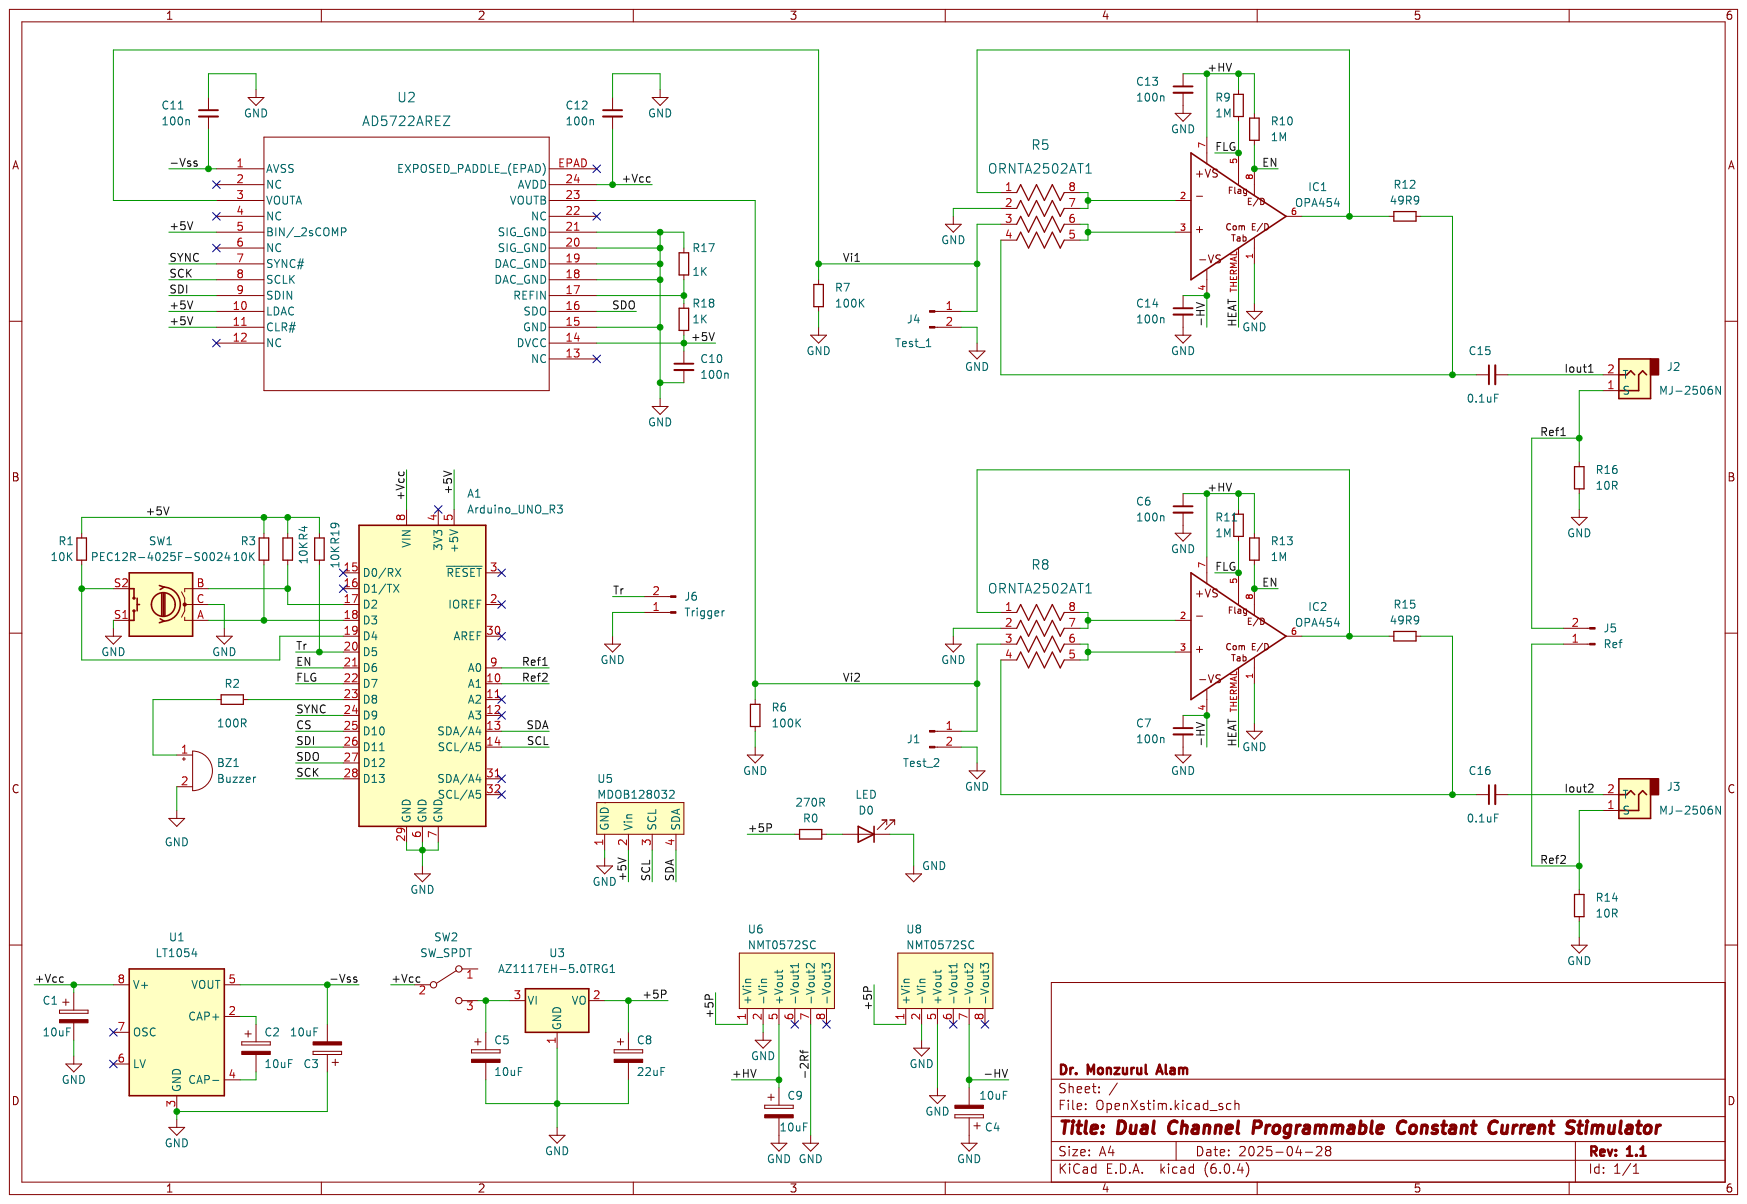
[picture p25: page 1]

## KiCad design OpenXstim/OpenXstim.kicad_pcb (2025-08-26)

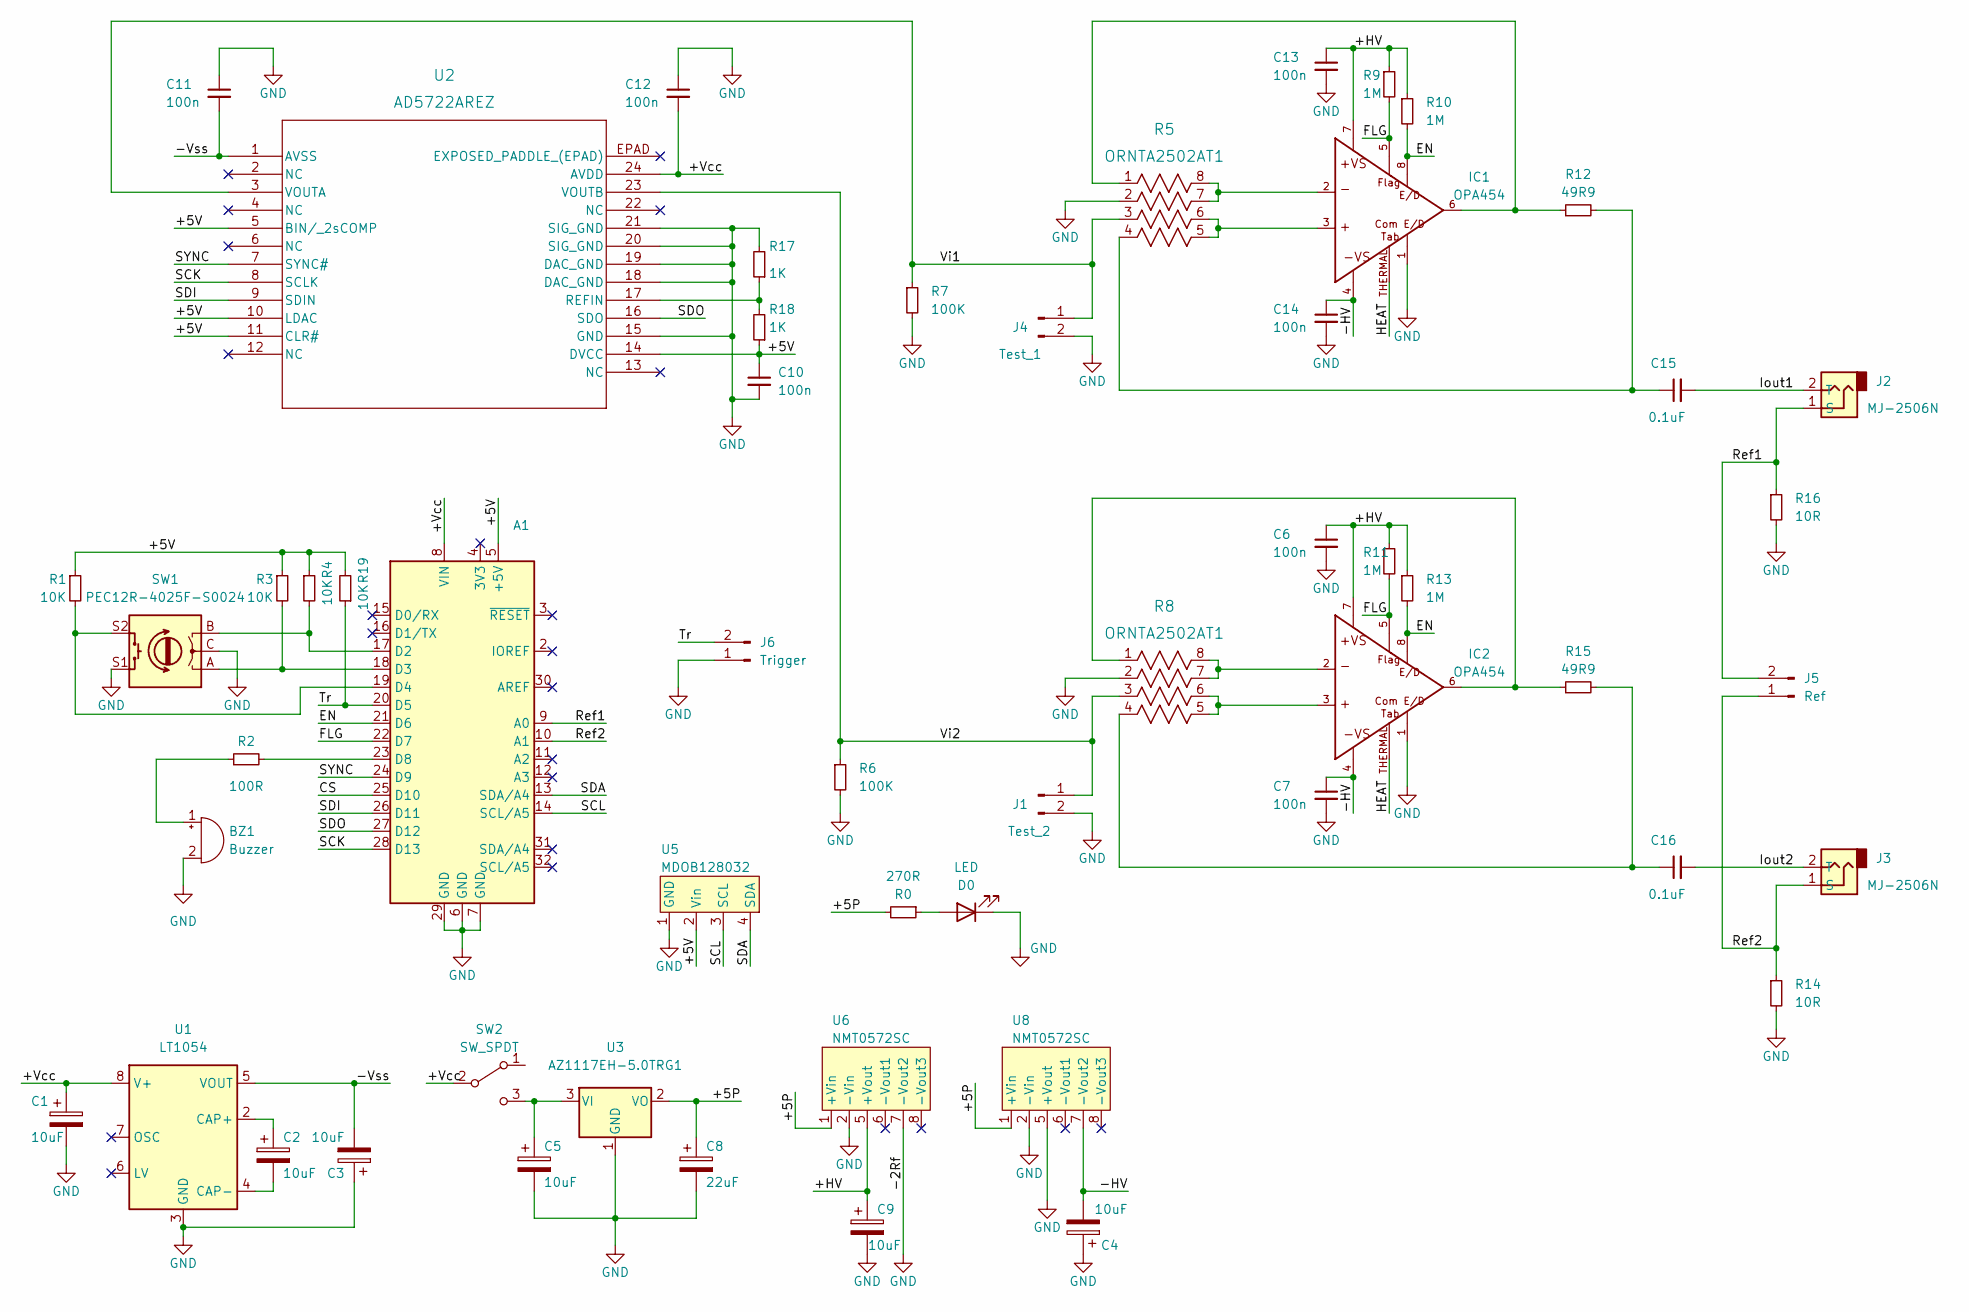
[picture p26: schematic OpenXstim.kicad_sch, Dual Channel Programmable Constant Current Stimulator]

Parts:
A1: (no value)
BZ1: Buzzer; Buzzer_12x9.5RM7.6
C1, C5: 10uF; C_1206_3216Metric
C2, C3: 10uF; CP_Elec_5x5.3
C4, C9: 10uF; CP_Elec_8x10.5
C6, C7, C10, C11, C12, C13, C14: 100n; C_0805_2012Metric
C8: 22uF; CP_Elec_5x5.4
C15, C16: 0.1uF; C_0805_2012Metric
D0: LED; LED_1206_3216Metric
IC1, IC2: OPA454; SO08GP; PARTNUM 296-22997-5-ND
J1: Test_2; PinHeader_1x02_P2.54mm_Vertical
J2, J3: MJ-2506N; CUI_MJ-2506N
J4: Test_1; PinHeader_1x02_P2.54mm_Vertical
J5: Ref; PinHeader_1x02_P2.54mm_Vertical
J6: Trigger; PinHeader_1x02_P2.54mm_Vertical
R0: 270R; R_0805_2012Metric
R1, R3, R4, R19: 10K; R_0805_2012Metric
R2: 100R; R_0805_2012Metric
R5, R8: ORNTA2502AT1; ORN_VIS
R6, R7: 100K; R_0805_2012Metric
R9, R10, R11, R13: 1M; R_0805_2012Metric
R12, R15: 49R9; R_0805_2012Metric
R14, R16: 10R; R_0805_2012Metric
R17, R18: 1K; R_0805_2012Metric
SW1: PEC12R-4025F-S0024; ENC_PEC12R-4025F-S0024
SW2: SW_SPDT; SW_MINI-SPDT-SW
U1: LT1054; SOIC-8_3.9x4.9mm_P1.27mm
U2: AD5722AREZ; RE_24_ADI
U3: AZ1117EH-5.0TRG1; SOT-223
U5: MDOB128032; MDOB128032GV-WI
U6, U8: NMT0572SC

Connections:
/+5P: C8.1, R0.2, U3.2 (VO), U6.1 (+Vin), U8.1 (+Vin)
/+5V: A1.5 (+5V), C10.1, R1.1, R3.1, R4.1, R18.1, R19.2, U2.5 (BIN/_2sCOMP), U2.10 (LDAC), U2.11 (CLR#), U2.14 (DVCC), U5.2 (Vin)
/+HV: C6.1, C9.1, C13.1, IC1.7, IC2.7, R9.1, R10.1, R11.1, R13.1, U6.5 (+Vout)
/+Vcc: A1.8 (VIN), C1.1, C12.2, SW2.2 (B), U1.8 (V+), U2.24 (AVDD)
/-HV: C4.2, C7.1, C14.1, IC1.4, IC2.4, U8.7 (-Vout2)
/-Vss: C3.2, C11.2, U1.5 (VOUT), U2.1 (AVSS)
/CS: A1.25 (D10)
/EN: A1.21 (D6), IC1.8, IC2.8, R10.2, R13.2
/FLG: A1.22 (D7), IC1.5, IC2.5, R9.2, R11.2
/HEAT: IC1.THERMAL, IC2.THERMAL
/Iout1: C15.2, J2.2 (T)
/Iout2: C16.2, J3.2 (T)
/Ref1: A1.9 (A0), J2.1 (S), J5.2, R16.1
/Ref2: A1.10 (A1), J3.1 (S), J5.1, R14.1
/SCK: A1.28 (D13), U2.8 (SCLK)
/SCL: A1.14 (SCL/A5), U5.3 (SCL)
/SDA: A1.13 (SDA/A4), U5.4 (SDA)
/SDI: A1.26 (D11), U2.9 (SDIN)
/SDO: A1.27 (D12), U2.16 (SDO)
/SYNC: A1.24 (D9), U2.7 (SYNC#)
/Tr: A1.20 (D5), J6.2, R19.1
/Vi1: J4.1, R5.3, R7.1, U2.3 (VOUTA)
/Vi2: J1.1, R6.1, R8.3, U2.23 (VOUTB)
GND: A1.6 (GND), A1.7 (GND), A1.29 (GND), BZ1.2 (+), C1.2, C3.1, C4.1, C5.2, C6.2, C7.2, C8.2, C9.2, C10.2, C11.1, C12.1, C13.2, C14.2, D0.1 (K), IC1.1, IC2.1, J1.2, J4.2, J6.1, R5.2, R6.2, R7.2, R8.2, R14.2, R16.2, R17.2, SW1.C, SW1.S1, U1.3 (GND), U2.15 (GND), U2.18 (DAC_GND), U2.19 (DAC_GND), U2.20 (SIG_GND), U2.21 (SIG_GND), U3.1 (GND), U5.1 (GND), U6.2 (-Vin), U6.7 (-Vout2), U8.2 (-Vin), U8.5 (+Vout)
unnamed: A1.17 (D2), R4.2, SW1.B
unnamed: A1.18 (D3), R3.2, SW1.A
unnamed: A1.19 (D4), R1.2, SW1.S2
unnamed: A1.23 (D8), R2.2
unnamed: BZ1.1 (-), R2.1
unnamed: C2.1, U1.2 (CAP+)
unnamed: C2.2, U1.4 (CAP-)
unnamed: C5.1, SW2.3 (C), U3.3 (VI)
unnamed: C15.1, R5.4, R12.2
unnamed: C16.1, R8.4, R15.2
unnamed: D0.2 (A), R0.1
unnamed: IC1.2, R5.7, R5.8
unnamed: IC1.3, R5.5, R5.6
unnamed: IC1.6, R5.1, R12.1
unnamed: IC2.2, R8.7, R8.8
unnamed: IC2.3, R8.5, R8.6
unnamed: IC2.6, R8.1, R15.1
unnamed: R17.1, R18.2, U2.17 (REFIN)

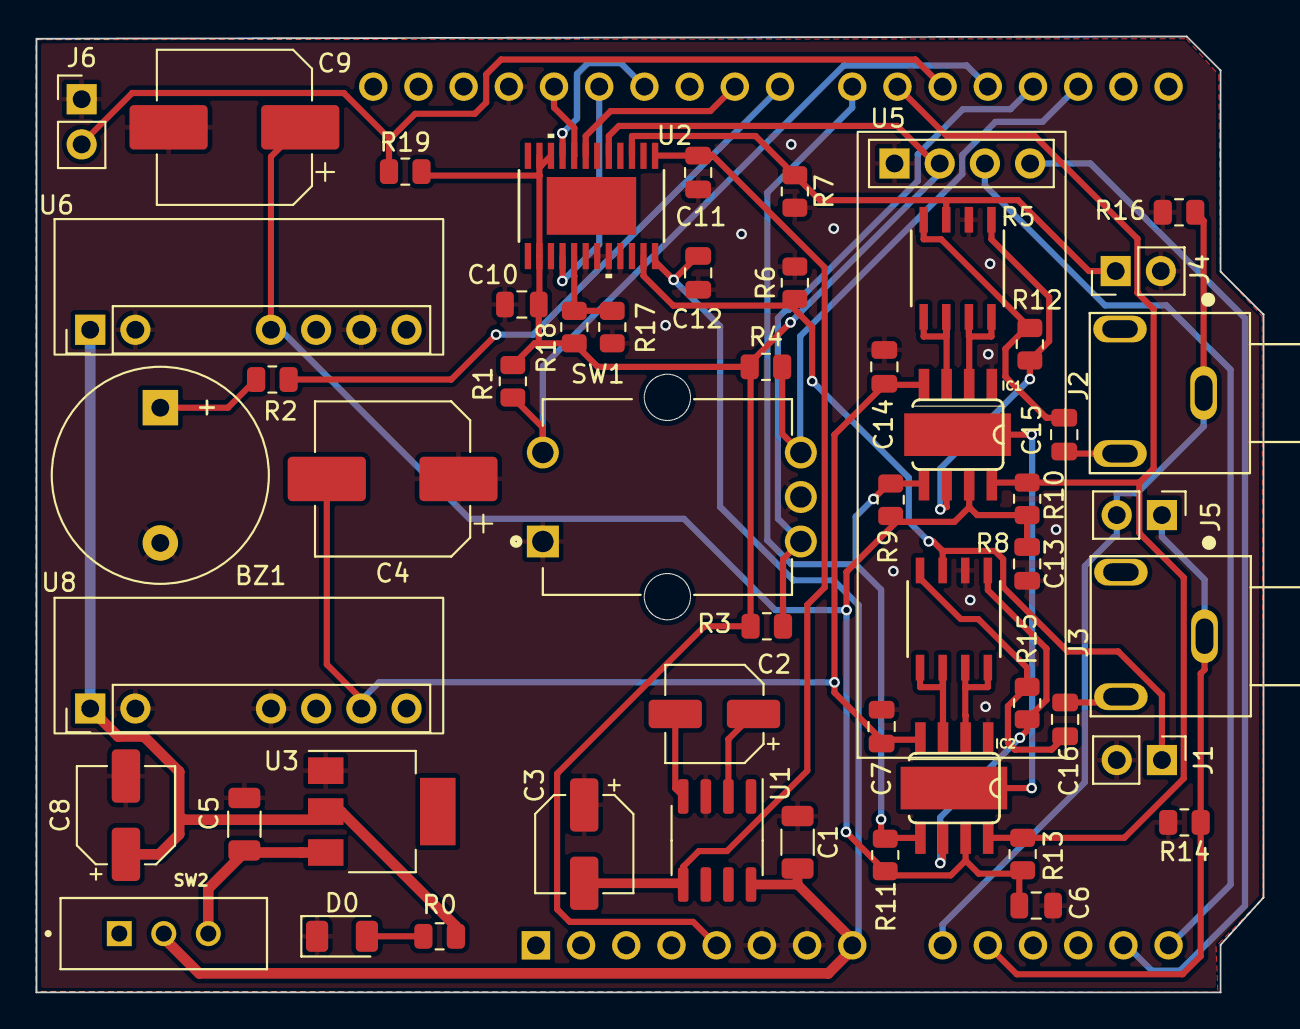
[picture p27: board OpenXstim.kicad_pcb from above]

Board: 2 copper layers, 69.0 x 53.7 mm, 55 parts (1 on the bottom side), 41 nets.

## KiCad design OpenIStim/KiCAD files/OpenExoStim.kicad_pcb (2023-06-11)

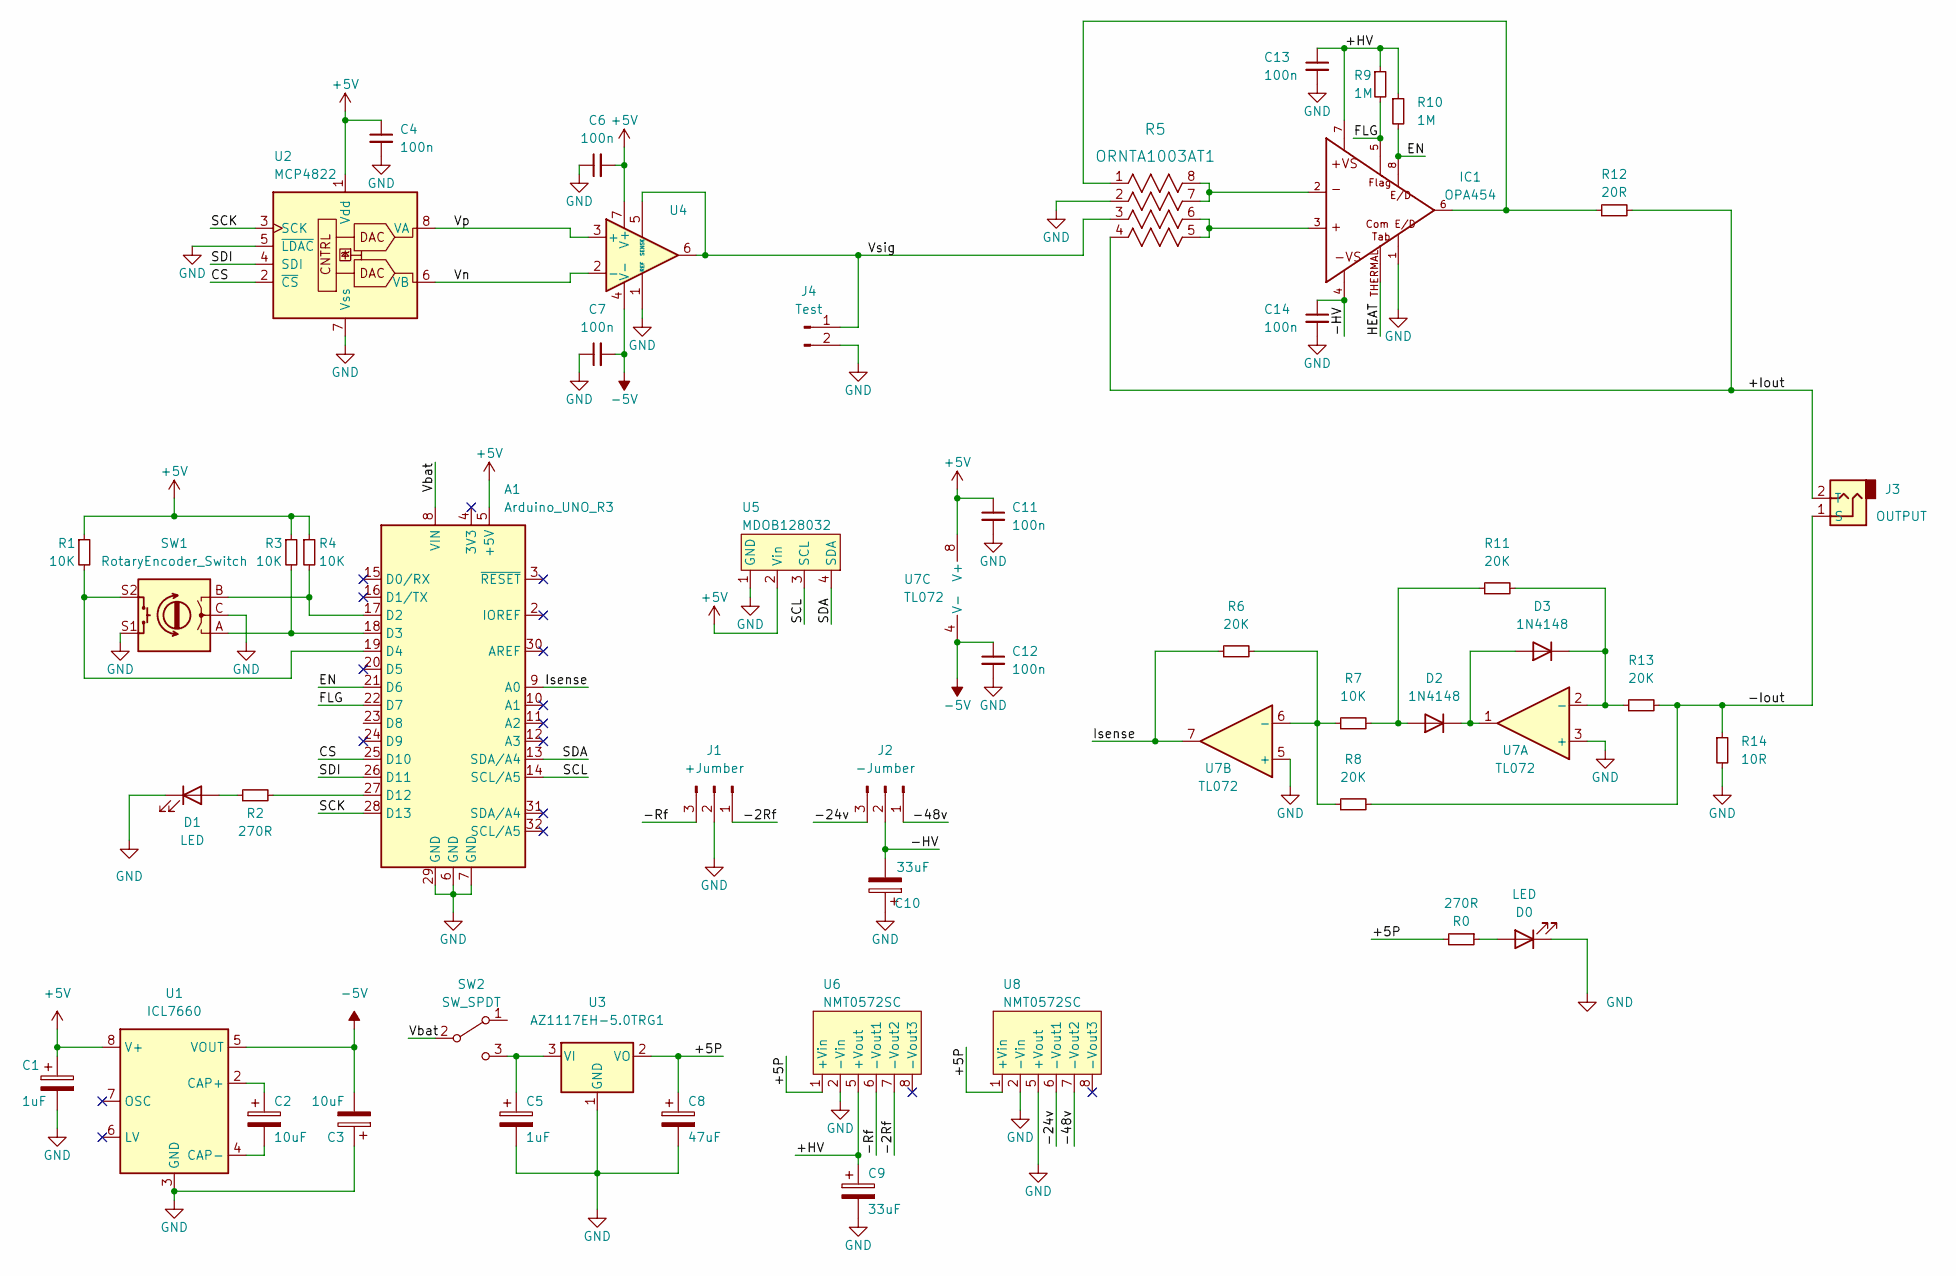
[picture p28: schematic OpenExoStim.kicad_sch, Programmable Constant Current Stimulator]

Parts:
A1: Arduino_UNO_R3
C1, C5: 1uF; C_1206_3216Metric
C2, C3: 10uF; CP_Elec_5x5.3
C4, C6, C7, C11, C12, C13, C14: 100n; C_0805_2012Metric
C8: 47uF; CP_Elec_5x5.4
C9, C10: 33uF; CP_Elec_8x10.5
D0, D1: LED; LED_1206_3216Metric
D2, D3: 1N4148; D_SOD-123
IC1: OPA454; SO08GP; PARTNUM 296-22997-5-ND
J1: +Jumber; PinHeader_1x03_P2.54mm_Vertical
J2: -Jumber; PinHeader_1x03_P2.54mm_Vertical
J3: OUTPUT; CUI_MJ-2506N
J4: Test; PinHeader_1x02_P2.54mm_Vertical
R0, R2: 270R; R_0805_2012Metric
R1, R3, R4, R7: 10K; R_0805_2012Metric
R5: ORNTA1003AT1; ORN_VIS
R6, R8, R11, R13: 20K; R_0805_2012Metric
R9, R10: 1M; R_0805_2012Metric
R12: 20R; R_Axial_DIN0207_L6.3mm_D2.5mm_P10.16mm_Horizontal
R14: 10R; R_Axial_DIN0207_L6.3mm_D2.5mm_P10.16mm_Horizontal
SW1: RotaryEncoder_Switch; ENC_PEC12R-4025F-S0024
SW2: SW_SPDT; SW_MINI-SPDT-SW
U1: ICL7660; SOIC-8_3.9x4.9mm_P1.27mm
U2: MCP4822; SOIC-8_3.9x4.9mm_P1.27mm
U3: AZ1117EH-5.0TRG1; SOT-223
U4: SOIC-8_3.9x4.9mm_P1.27mm
U5: MDOB128032; MDOB128032GV-WI
U6, U8: NMT0572SC
U7: TL072; SOIC-8_3.9x4.9mm_P1.27mm

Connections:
+5V: A1.5 (+5V), C1.1, C4.1, C6.2, C11.1, R1.1, R3.1, R4.1, U1.8 (V+), U2.1 (Vdd), U4.7 (V+), U5.2 (Vin), U7.8 (V+)
-5V: C3.2, C7.2, C12.1, U1.5 (VOUT), U4.4 (V-), U7.4 (V-)
/+5P: C8.1, R0.2, U3.2 (VO), U6.1 (+Vin), U8.1 (+Vin)
/+HV: C9.1, C13.1, IC1.7, R9.1, R10.1, U6.5 (+Vout)
/+Iout: J3.2 (T), R5.4, R12.2
/-2Rf: J1.1, U6.7 (-Vout2)
/-24v: J2.3, U8.6 (-Vout1)
/-48v: J2.1, U8.7 (-Vout2)
/-HV: C10.2, C14.1, IC1.4, J2.2
/-Iout: J3.1 (S), R8.2, R13.2, R14.1
/-Rf: J1.3, U6.6 (-Vout1)
/CS: A1.25 (D10), U2.2 (~CS)
/EN: A1.21 (D6), IC1.8, R10.2
/FLG: A1.22 (D7), IC1.5, R9.2
/HEAT: IC1.THERMAL
/Isense: A1.9 (A0), R6.1, U7.7
/SCK: A1.28 (D13), U2.3 (SCK)
/SCL: A1.14 (SCL/A5), U5.3 (SCL)
/SDA: A1.13 (SDA/A4), U5.4 (SDA)
/SDI: A1.26 (D11), U2.4 (SDI)
/Vbat: A1.8 (VIN), SW2.2 (B)
/Vn: U2.6 (VB), U4.2 (-)
/Vp: U2.8 (VA), U4.3 (+)
/Vsig: J4.1, R5.3, U4.5 (SENSE), U4.6
GND: A1.6 (GND), A1.7 (GND), A1.29 (GND), C1.2, C3.1, C4.2, C5.2, C6.1, C7.1, C8.2, C9.2, C10.1, C11.2, C12.2, C13.2, C14.2, D0.1 (K), D1.1 (K), IC1.1, J1.2, J4.2, R5.2, R14.2, SW1.C, SW1.S1, U1.3 (GND), U2.5 (~LDAC), U2.7 (Vss), U3.1 (GND), U4.1 (REF), U5.1 (GND), U6.2 (-Vin), U7.3 (+), U7.5 (+), U8.2 (-Vin), U8.5 (+Vout)
unnamed: A1.17 (D2), R4.2, SW1.B
unnamed: A1.18 (D3), R3.2, SW1.A
unnamed: A1.19 (D4), R1.2, SW1.S2
unnamed: A1.27 (D12), R2.2
unnamed: C2.1, U1.2 (CAP+)
unnamed: C2.2, U1.4 (CAP-)
unnamed: C5.1, SW2.3 (C), U3.3 (VI)
unnamed: D0.2 (A), R0.1
unnamed: D1.2 (A), R2.1
unnamed: D2.1 (K), D3.2 (A), U7.1
unnamed: D2.2 (A), R7.2, R11.1
unnamed: D3.1 (K), R11.2, R13.1, U7.2 (-)
unnamed: IC1.2, R5.7, R5.8
unnamed: IC1.3, R5.5, R5.6
unnamed: IC1.6, R5.1, R12.1
unnamed: R6.2, R7.1, R8.1, U7.6 (-)

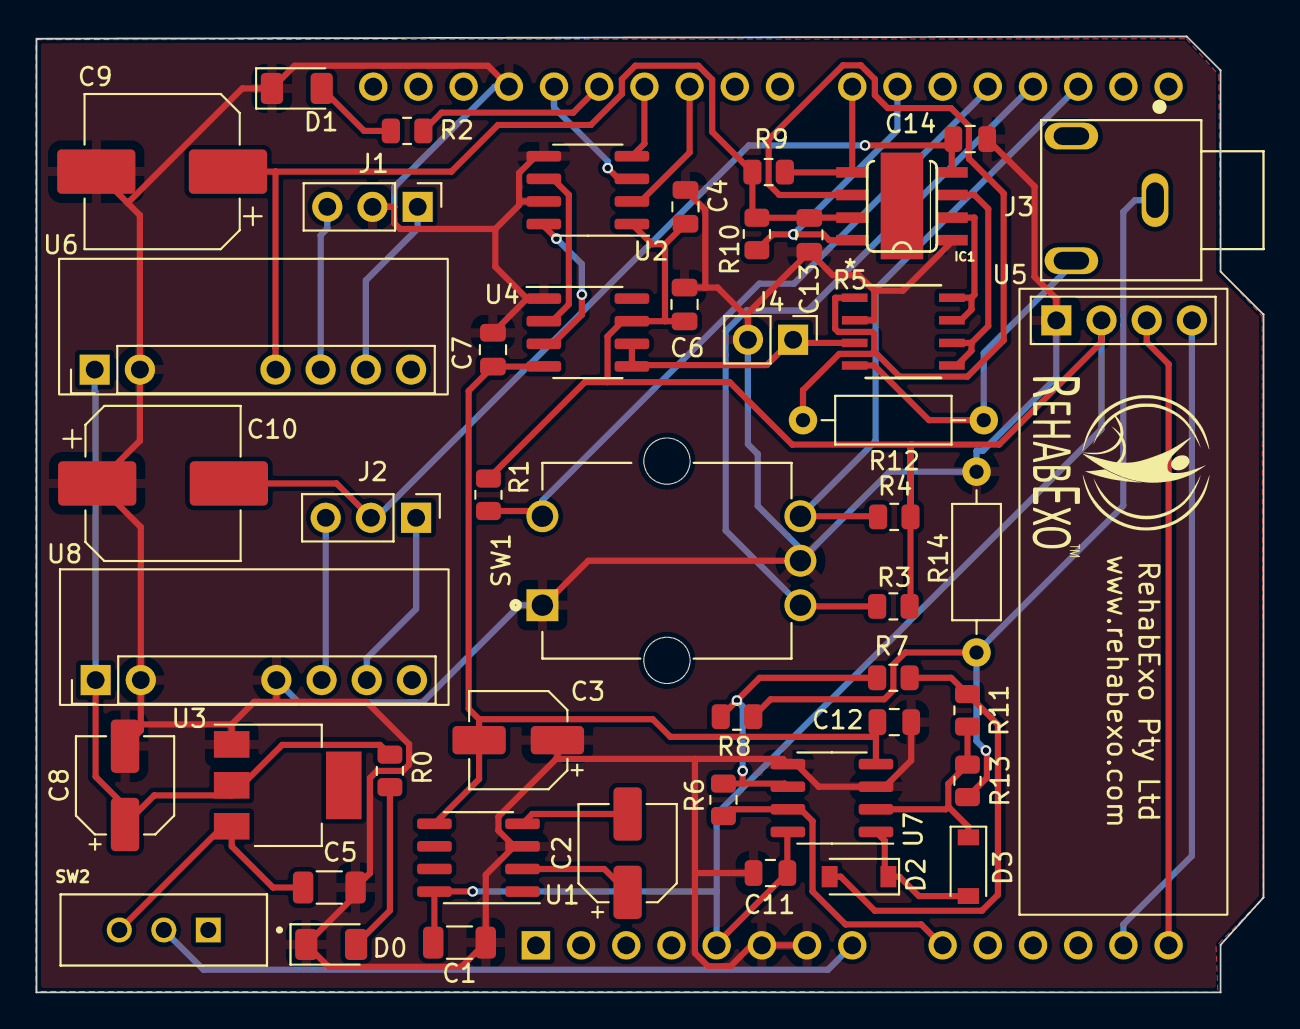
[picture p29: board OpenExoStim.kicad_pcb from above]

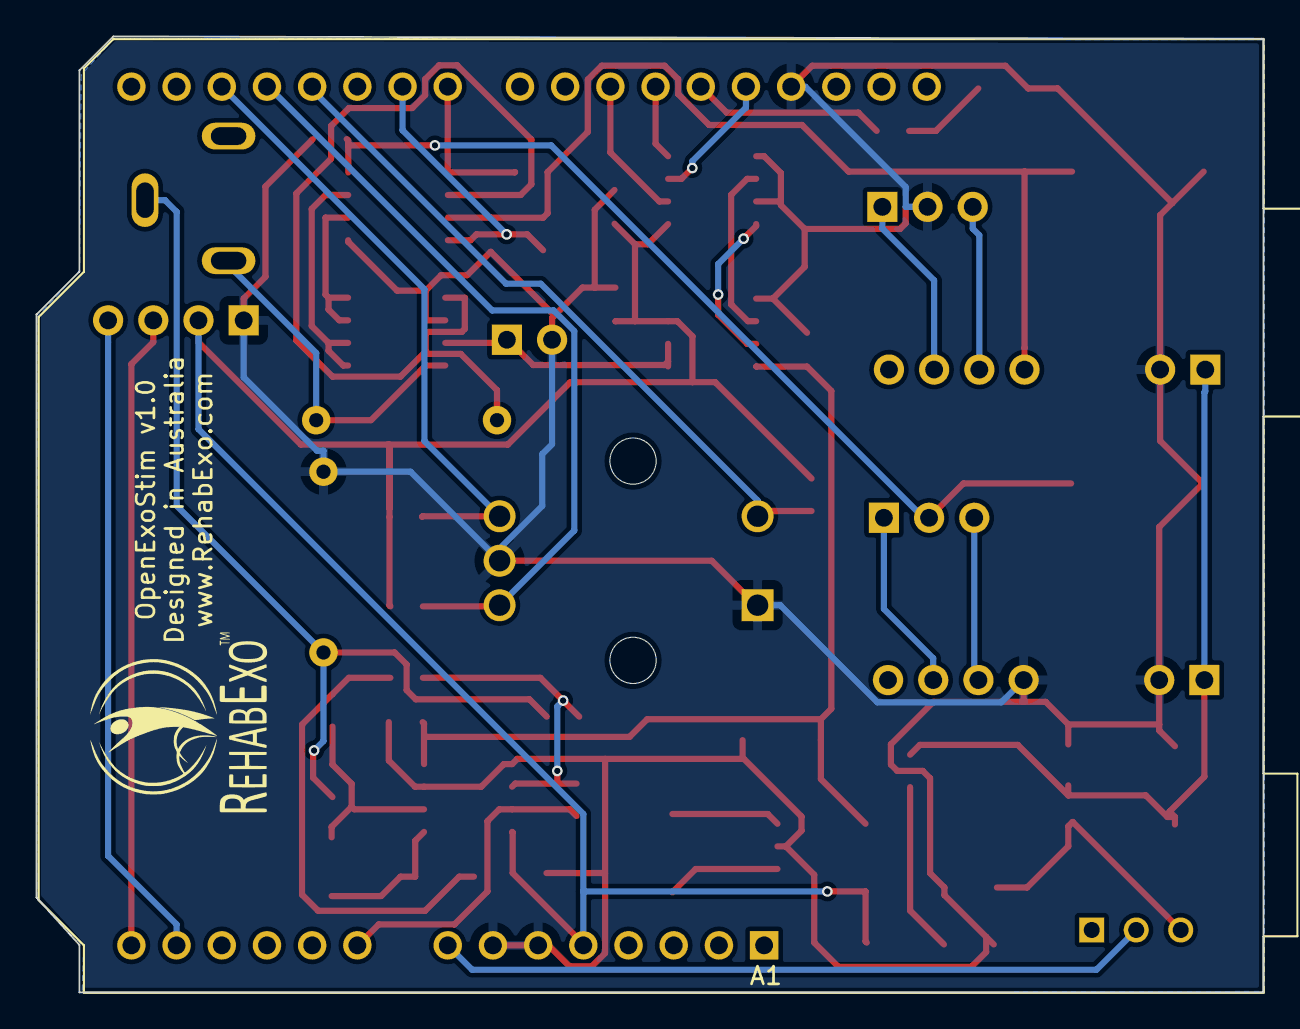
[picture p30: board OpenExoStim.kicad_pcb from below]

Board: 2 copper layers, 69.0 x 53.7 mm, 51 parts (2 on the bottom side), 40 nets.

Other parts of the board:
G1, G2: LOGO; RehabExoNameLogo_11mmx15.6mm
